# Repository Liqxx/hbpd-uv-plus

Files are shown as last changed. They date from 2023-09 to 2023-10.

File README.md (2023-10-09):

# HBPD-UV+ light pulsers

This repository describes the sub-ns and high-power UV/Vis pulsed diode design package **HBPD-UV+** developed by Felix Henningsen and Nicolas Braam.

## Contact
* Felix Henningsen (felix_henningsen@sfu.ca)
* Nicolas Braam (nbraam@uvic.ca)

## Warning
The drivers described in this repository carry the potential to emit intense ultraviolet light and high peak-power laser radiation when used with light emitting diodes or laser diodes. Exposure to these optical pulses can lead to adverse health effects and permanent vision damage.

It is the user's full responsibility to adhere to appropriate laser safety procedures to avoid any eye or skin exposure and related health consequences.

## Folder structure
#### sub-ns/
* [firmware/](sub-ns/firmware) - Microcontroller firmware
* [manufacture/](sub-ns/manufacture) - Manufacturing files for the printed circuit board design
* [schematic/](sub-ns/schematic) - Schematics for the printed circuit board design
* [userguide/](sub-ns/userguide) - User guide

#### high-power/
* [manufacture/](high-power/manufacture) - Manufacturing files for the printed circuit board design
* [schematic/](high-power/schematic) - Schematics for the printed circuit board design

## File viewer
For viewing the manufacturing Gerber RS-274X files, we recommend the open-source gerber file viewer https://github.com/gerbv/gerbv, or your preferred electronics design software.

## Citation
F. Henningsen, N. Braam *et al* 2023 *JINST* **18** P10010

**DOI** [10.1088/1748-0221/18/10/P10010](https://iopscience.iop.org/article/10.1088/1748-0221/18/10/P10010)

## Licence
Licensing differs for the various sub-components, and license information for all individual packages is included in the respective sub-directories.

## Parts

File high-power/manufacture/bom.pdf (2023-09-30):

## High-power pulser BOM

Part | Populate | Manufacturer | Manufacturer Part # | Supplier | Supplier Part # | Supplier Description | Quantity per Unit
C1,C2,C3,C4 | Yes | Murata Electronics | GRM21BD72A225KE01L | Digikey | 490-GRM21BD72A225KE01LDKR-ND | 2.2 µF ±10% 100V Ceramic Capacitor X7T 0805 (2012 Metric) | 4
C5, C6, C7, C8 | Yes | Murata Electronics | GRM188Z71E225KE43D | Digikey | 490-GRM188Z71E225KE43DTR-ND | 2.2 µF ±10% 25V Ceramic Capacitor X7R 0603 (1608 Metric) | 4
C9,C10,C11,C12,C13 Yes | Samsung Electro-Mechanics | CL10B105KA8NFNC | Digikey | 1276-1942-6-ND | 1 µF ±10% 25V Ceramic Capacitor X7R 0603 (1608 Metric) | 5
C14,C15 | Yes | Vishay Vitramon | VJ0603A120FXXPW1BC | Digikey | 720-VJ0603A120FXXPW1BCDKR-ND | 12 pF ±1% 25V Ceramic Capacitor C0G, NP0 0603 (1608 Metric) | 2
C16,C17 | Yes | Murata Electronics | GCM1555C1H5R0FA16D | Digikey | 490-GCM1555C1H5R0FA16DDKR-ND 5 pF ±1% 50V Ceramic Capacitor C0G, NP0 0402 (1005 Metric) | 2
C18,C19,C20,C21 | Yes | Samsung Electro-Mechanics | CL10B104KC8NNNC | Digikey | 1276-6807-6-ND | 0.1 µF ±10% 100V Ceramic Capacitor X7R 0603 (1608 Metric) | 4
C22 | Yes | Taiyo Yuden | HMK105B7103KVHFE | Digikey | 587-HMK105B7103KVHFECT-ND | 10000 pF ±10% 100V Ceramic Capacitor X7R 0402 (1005 Metric) | 1
C23,C24,C25 | Yes | YAGEO | CC0402KPX7R8BB104 | Digikey | 13-CC0402KPX7R8BB104DKR-ND | 0.1 µF ±10% 25V Ceramic Capacitor X7R 0402 (1005 Metric) | 3
C26 | Yes | TDK Corporation | C0510X5R1C104M030BC | Digikey | 445-13583-6-ND | 0.1 µF ±20% 16V Ceramic Capacitor X5R 0204 (0510 Metric) | 1
D1 | Yes | Rohm | RF05VAM2STR | Digikey | RF05VAM2STR-ND | Diode 200 V 500mA Surface Mount TUMD2S | 1
FB1,FB2,FB3 | Yes | TDK | MPZ1005S331ET000 | Digikey | 445-9330-2-ND | 330 Ohms 1 Power Line Ferrite Bead 0402 (1005 Metric) 700mA 280mOhm | 3
J1,J2 | Yes | TE Connectivity | 1776113-2 | Digikey | A97976-ND | 2 Position Wire to Board Terminal Block Horizontal with Board 0.150" (3.81mm) Through Hole | 2
J3,J5 | Yes | Samtec | MMCX-J-P-H-ST-SM1 | Digikey | SAM8838-ND | MMCX Connector Jack, Female Socket 50Ohm Surface Mount Solder | 2
L1 | Yes | Murata Electronics | LQW18AS3N6G0ZD | Digikey | 490-15826-6-ND | 3.6 nH Unshielded Wirewound Inductor 700 mA 63mOhm Max 0603 (1608 Metric) | 1
Q1 | Yes | EPC | EPC2214 | Digikey | 917-1213-2-ND | N-Channel 80 V 10A (Ta) Surface Mount Die | 1
R1 | Yes | Vishay Dale | RCA080549R9FKEA | Digikey | 541-2220-2-ND | 49.9 Ohms ±1% 0.125W, 1/8W Chip Resistor 0805 (2012 Metric) Anti-Sulfur, Automotive AEC-Q200 Thick Film | 1
R2,R4 | Yes | YAGEO | AC0603FR-07100RL | Digikey | YAG3561DKR-ND | 100 Ohms ±1% 0.1W, 1/10W Chip Resistor 0603 (1608 Metric) Automotive AEC-Q200, Moisture Resistant Thick Film | 2
R3 | Yes | YAGEO | RC0603FR-1356RL | Digikey | 13-RC0603FR-1356RLDKR-ND | 56 Ohms ±1% 0.1W, 1/10W Chip Resistor 0603 (1608 Metric) Thick Film | 1
R5,R6,R7,R8 | Yes | Vishay Dale | CRCW04023R90FKED | Digikey | 541-3.90LLTR-ND | 3.9 Ohms ±1% 0.063W, 1/16W Chip Resistor 0402 (1005 Metric) Automotive AEC-Q200 Thick Film | 4
R9 | Yes | Keystone Electronics | 5108 | Digikey | 36-5108TR-ND | 0 Ohms Jumper Chip Resistor 1206 (3216 Metric) Metal Element | 1
R10 | Yes | Vishay Dale | CRCW0603100KFKEAHP | Digikey | 541-100KSTR-ND | 100 kOhms ±1% 0.333W, 1/3W Chip Resistor 0603 (1608 Metric) Automotive AEC-Q200, Pulse Withstanding Thick Film | 1
R11,R12 | Yes | Stackpole Electronics Inc | RMCF0201ZT0R00 | Digikey | RMCF0201ZT0R00DKR-ND | 0 Ohms Jumper Chip Resistor 0201 (0603 Metric) Thick Film | 2
R13,R14 | Yes | Vishay Dale | CRCW040210R0FKEE | Digikey | 541-CRCW040210R0FKEETR-ND | 10 Ohms ±1% 0.063W, 1/16W Chip Resistor 0402 (1005 Metric) Automotive AEC-Q200 Thick Film | 2
R15 | No | - | - | - | - | | -
R16 | Yes | YAGEO | RC0603FR-072R4L | Digikey | 13-RC0603FR-072R4LTR-ND | 2.4 Ohms ±1% 0.1W, 1/10W Chip Resistor 0603 (1608 Metric) Moisture Resistant Thick Film | 1
R17 | Yes | Panasonic | ERA-2AEB102X | Digikey | P1.0KDCTR-ND | 1 kOhms ±0.1% 0.063W, 1/16W Chip Resistor 0402 (1005 Metric) Automotive AEC-Q200 Thin Film | 1
R18 | Yes | Panasonic | ERA-2AEB49R9X | Digikey | P49.9DCTR-ND | 49.9 Ohms ±0.1% 0.063W, 1/16W Chip Resistor 0402 (1005 Metric) Automotive AEC-Q200 Thin Film | 1
U1 | Yes | Microchip Technology | MCP1703T-5002E/MC | Digikey | MCP1703T-5002E/MCTR-ND | Linear Voltage Regulator IC Positive Fixed 1 Output 250mA 8-DFN (2x3) | 1
U2 | No | Microchip Technology | MCP1703T-3302E/CB | - | - | | -
U3,U4 | Yes | onsemi | NC7WZ16L6X | Digikey | NC7WZ16L6XTR-ND | Buffer, Non-Inverting 2 Element 1 Bit per Element Push-Pull Output 6-MicroPak | 2
U5 | Yes | Texas Instruments | LMG1020YFFR | Digikey | 296-50208-2-ND | Low-Side Gate Driver IC Inverting, Non-Inverting 6-DSBGA | 1
| | | | | | | 58

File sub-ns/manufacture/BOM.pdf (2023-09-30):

## LED Pulser BOM:

Electronic Components

Part Reference | Manufacturer | Manufacturer Part # | Description | Supplier | Supplier Part #

Quantity
for One
Unit
C1,C17,C29,C44,C60,C64,C66,C70,C71,C72,C73,C74,C75,C76 | Murata Electronics | GCM155R71H104KE02J | CAP CER 0.1UF 50V X7R 0402 | Digikey | 490‐14514‐1‐ND | 14
C2,C18,C30,C45,C61,C65,C67,C68,C69 | Samsung Electro‐Mechanics | CL10B105MO8NNWC | CAP CER 1UF 16V X7R 0603 | Digikey | 1276‐6524‐1‐ND | 9
C3,C10,C19,C24,C31,C38,C46 | TDK Corporation | C0510X5R0J105M030BC | CAP CER 1UF 6.3V X5R 0204 | Digikey | 445‐9091‐1‐ND | 7
C4,C11,C20,C25,C32,C39,C47 | Murata Electronics | NFM15PC474R0J3D | CAP FEEDTHRU 0.47UF 6.3V 0402 | Digikey | 490‐16920‐1‐ND | 7
C5,C6,C12,C13,C21,C22,C26,C27,C33,C34,C40,C41,C48,C49,C77,C78,C79,C80,C81,C82,C83 | TDK Corporation | C0510X7R1E473M030BA | CAP CER 0.047UF 25V X7R 0204 | Digikey | 445‐C0510X7R1E473M030BACT‐ND | 21
C7,C9,C14,C16,C35,C37,C42 | Murata Electronics | GCM155R71E103KA37D | CAP CER 10000PF 25V X7R 0402 | Digikey | 490‐6043‐1‐ND | 7
C8,C15,C23,C28,C36,C43,C50 | KYOCERA AVX | 0201ZK4R7BBSTR | CAP THIN FILM 4.7PF 10V 0201 | Digikey | 478‐4386‐1‐ND | 7
C51,C53,C62,C63 | TDK Corporation | C2012X5R1E475K125AB | CAP CER 4.7UF 25V X5R 0805 | Digikey | 445‐4116‐1‐ND | 4
C52,C57,C59 | Murata Electronics | GCM155R71H103KA55D | CAP CER 10000PF 50V X7R 0402 | Digikey | 490‐4762‐1‐ND | 3
C54,C55,C56,C58 | TDK Corporation | CGA4J1X7S1E106K125AC | CAP CER 10UF 25V X7S 0805 | Digikey | 445‐181405‐1‐ND | 4
D1 | Rohm Semiconductor | SML013BNTT86 | CHIP LED WITH REFLECTOR: SML‐01 | Digikey | 846‐SML013BNTT86CT‐ND | 1
D2 | Vishay Semiconductor Opto Division | VLMU3100‐GS08 | EMITTER UV 405NM 30MA PLCC | Digikey | VLMU3100‐GS08CT‐ND | 1
D3 | LC LED | UT‐69UV365P | LED 0603 UV SMD LED 365nm | LC LED | UT‐69UV365P | 1
D4 | Photon Wave | PKE‐02‐F35 | LED 295nm 15mW 3535 | IRTRONIX Inc | PKE‐10‐F35 | 1
D5 | Photon Wave | PKD‐02‐F35 | LED 278nm 3.5mW 3535 | IRTRONIX Inc | PKD‐02‐F35 | 1
D6 | Photon Wave | PKB‐02‐F35 | LED 255nm 3.5mW 3535 | IRTRONIX Inc | PKB‐02‐F35 | 1
D7 | Silanna UV | SF1‐3C3FWL1 | LED 235nm 0.45mW 3535 | Silanna UV | SF1‐3C3FWL1‐TR | 1
D8 | SMC Diode Solutions | DSS14U | SCHOTTKY 40V SOD‐123FL | Digikey | 1655‐DSS14UCT‐ND | 1
D9 | Diodes Incorporated | SMAJ5.0A‐13‐F | TVS DIODE 5VWM 9.2VC SMA | Digikey | SMAJ5.0A‐FDICT‐ND | 1
D10,D11,D12,D13 | Semtech Corporation | RCLAMP3331ZATFT | TVS DIODE 3.3V 7.5V SLP0603P2X3F | Digikey | RCLAMP3331ZATFTCT‐ND | 4
J1,J2,J3,J4,J5,J6,J7 | Molex | 734152063 | CONN MMCX JACK STR 50 OHM SMD | Digikey | WM3914CT‐ND | 7
J8 | CUI Inc. | PJ‐037AH | CONN PWR JACK 2X5.5MM SOLDER | Digikey | CP‐037AH‐ND | 1
J9,J10 | Molex | 734152063 | CONN MMCX JACK STR 50 OHM SMD | Digikey | WM3914CT‐ND | 2
J11 | METZ CONNECT USA Inc. | PR20204VBNN | PIN HEADER, THR, SINGLE ROW, .10 | Digikey | 1849‐PR20204VBNN‐ND | 1
J12 | Amphenol ICC (FCI) | 78208‐106HLF | CONN HEADER R/A 6POS 2.54MM | Digikey | 609‐2452‐ND | 1
L1,L2,L3,L4,L5,L6,L7 | Delta Electronics/Components | 0402HC‐3N6EDTS | FIXED IND 3.6NH 900MA 40MOHM SMD | Digikey | 2035‐1343‐1‐ND | 7
L8 | Sumida America Components Inc. | CDRH4D16FB/NP‐100MC | FIXED IND 10UH 1.2A 118 MOHM SMD | Digikey | 308‐2011‐1‐ND | 1
Q1,Q2,Q3,Q4,Q5,Q6,Q7 | EPC | EPC8004 | GANFET N‐CH 40V 4A DIE | Digikey | 917‐1072‐1‐ND | 7
R3,R9,R23,R27,R35,R41,R53,R67,R73 | Yageo | RC0402FR‐07100RL | RES SMD 100 OHM 1% 1/16W 0402 | Digikey | 311‐100LRCT‐ND | 9
R4,R6,R14,R16,R24,R25,R30,R31,R36,R37,R46,R48,R54,R55 | Vishay Dale | CRCW02012R00FXED | RES SMD 2 OHM 1% 1/20W 0201 | Digikey | 541‐CRCW02012R00FXEDCT‐ND | 14
R5,R10,R15,R19,R38,R42,R47,R72,R74 | YAGEO | RC0402FR‐071KL | RES 1K OHM 1% 1/16W 0402 | Digikey | 311‐1.00KLRCT‐ND | 9
R7,R18,R26,R32,R39,R50,R56 | Vishay Dale | CRCW020168R0FKED | RES SMD 68 OHM 1% 1/20W 0201 | Digikey | 541‐68.0AABCT‐ND | 7
R8,R12,R17,R20,R40,R44,R49 | YAGEO | RC0402FR‐0749R9L | RES 49.9 OHM 1% 1/16W 0402 | Digikey | 311‐49.9LRCT‐ND | 7
R2,R13,R29,R34,R45,R52 | YAGEO | RC0402JR‐074R3L | RES 4.3 OHM 5% 1/16W 0402 | Digikey | 311‐4.3JRCT‐ND | 6
R22 | YAGEO | RC0402JR‐072R2L | RES 2.2 OHM 5% 1/16W 0402 | Digikey | 311‐2.2JRCT‐ND | 1
R58 | Bel Fuse Inc. | 0ZCF0030FF2C | PTC RESET FUSE 60V 300MA 2920 | Digikey | 507‐1740‐1‐ND | 1
R59 | Samsung Electro‐Mechanics | RC1005F205CS | RES SMD 2M OHM 1% 1/16W 0402 | Digikey | 1276‐4293‐1‐ND | 1
R60,R65,R66,R69,R71,R80 | Samsung Electro‐Mechanics | RC1005F103CS | RES SMD 10K OHM 1% 1/16W 0402 | Digikey | 1276‐3431‐1‐ND | 6
R62 | YAGEO | RC0402FR‐07169KL | RES 169K OHM 1% 1/16W 0402 | Digikey | YAG3000CT‐ND | 1
R63 | YAGEO | RC0402FR‐07200KL | RES 200K OHM 1% 1/16W 0402 | Digikey | 311‐200KLRCT‐ND | 1
R64 | YAGEO | RC0402FR‐0753K6L | RES 53.6K OHM 1% 1/16W 0402 | Digikey | 311‐53.6KLRCT‐ND | 1
R68 | Yageo | RC0805FR‐130RL | RES 0 OHM JUMPER 1/8W 0805 | Digikey | 13‐RC0805FR‐130RLCT‐ND | 1
R70 | Yageo | RC0805FR‐0749R9L | RES SMD 49.9 OHM 1% 1/8W 0805 | Digikey | 311‐49.9CRCT‐ND | 1
R76 | YAGEO | RC0402FR‐07330RL | RES 330 OHM 1% 1/16W 0402 | Digikey | 311‐330LRCT‐ND | 1
R77 | YAGEO | RC0402FR‐0740K2L | RES 40.2K OHM 1% 1/16W 0402 | Digikey | 311‐40.2KLRCT‐ND | 1
U1,U4,U8,U11 | Texas Instruments | DS90C402MX/NOPB | IC RECEIVER 0/2 8SOIC | Digikey | 296‐35381‐1‐ND | 4
U2,U3,U5,U6,U7,U9,U10 | Texas Instruments | LMG1020YFFR | IC GATE DRVR LOW‐SIDE 6DSBGA | Digikey | 296‐50208‐1‐ND | 7
U12 | Diodes Incorporated | AP3015AKTR‐G1 | IC REG BOOST ADJ 75MA SOT23‐5 | Digikey | AP3015AKTR‐G1DICT‐ND | 1
U13 | Analog Devices Inc. | ADP122AUJZ‐3.3‐R7 | IC REG LINEAR 3.3V 300MA TSOT5 | Digikey | 505‐ADP122AUJZ‐3.3‐R7CT‐ND | 1
U14 | Analog Devices Inc. | LT3061EMS8E#TRPBF | IC REG LIN POS ADJ 100MA 8MSOP | Digikey | LT3061EMS8E#TRPBFCT‐ND | 1
U15 | Texas Instruments | DS90LV018ATMX/NOPB | IC RECEIVER 0/1 8SOIC | Digikey | DS90LV018ATMX/NOPBCT‐ND | 1
U16 | Analog Devices Inc. | ADP7118AUJZ‐5.0‐R7 | IC REG LINEAR 5V 200MA TSOT23‐5 | Digikey | 505‐ADP7118AUJZ‐5.0‐R7CT‐ND | 1
U18 | Diodes Incorporated | AP22804AW5‐7 | IC PWR SWITCH P‐CHAN 1:1 SOT25 | Digikey | AP22804AW5‐7DICT‐ND | 1
U17 | Texas Instruments | DS90LV011AQMFE/NOPB | IC DRIVER 1/0 SOT23‐5 | Digikey | DS90LV011AQMFE/NOPBCT‐ND | 1
U19 | Microchip Technology | AVR64DD32‐I/RXB | 64KB, 8KB RAM, 32P, 24MHZ, MVIO, | Digikey | 150‐AVR64DD32‐I/RXB‐ND | 1
U20 | Skyworks Solutions, Inc. | SI53315‐B‐GM | Clock Buffer Universal 2:10 low‐jitter clock buffer/leve Mouser | 634‐SI53315‐B‐GM | 1
Y1 | Murata Electronics | CSTNE24M0VH3C000R0 | 3.2X1.3MM 24.0MHZ CERAMIC RESONA | Digikey | 490‐CSTNE24M0VH3C000R0CT‐ND | 1

Power Adapter, Comm Cable, Fibers:
Part Reference Manufacturer Manufacturer Part # Description Supplier Supplier Part # | Quantity for One Unit
J12 FTDI TTL‐232R‐3V3 CABLE USB EMBD UART 3.3V .1"HDR Digikey 768‐1015‐ND D1 Thorlabs M80L005 Ø200 µm Core, 0.22 NA, FC/PC to Ø2.5 mm Ferrule PatThorlabs M80L005 Taoglas Limited CAB.01402 CBL ASSY SMA‐MMCX RG174 3.937" Digikey 931‐1099‐ND D1 Bivar Inc. SMFLP36.0 LIGHT PIPE FLEXIBLE CLEAR 4MM Digikey SMFLP36.0‐ND J8 CUI Inc. SWI6‐5.9‐N‐P7 AC/DC WALL MNT ADAPTER 5.9V 7.1W Digikey 102‐3608‐ND | 1 1 2 1 1

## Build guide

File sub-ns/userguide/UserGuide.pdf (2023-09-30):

# Light Source User Guide

## Hardware Specification

‐ | Seven LEDs: 468nm, 410nm, 367nm, 295nm, 275nm, 255nm, 235nm
‐ | LEDs flash for <1ns (FWHM)
‐ | Seven (optional) LED cathode MMCX test points to observe LED cathode electronic pulse
‐ | External desktop power adapter
‐ | External Trigger input MMCX coax connector
‐ | DAQ Sync output MMCX coax connector
‐ | Computer control via Serial UART port of: • LED Bias Voltage setting (10 bit DAC)
| • LED Bias Voltage read back (12 bit ADC)
| • LED Channel selection
| • LED Trigger source (external, or internal)
| • Internal trigger rate (fast or slow)
| • Power Down (for standby, low power consumption)

## General Description

The Light Source is designed to operate in a standalone fashion, or with integration to external systems. In standalone fashion, it only needs power, and a serial connection to a computer. If integrated to other systems, it can additionally accept an external trigger, and provides a sync output to DAQ electronics.

Seven LEDs of interest are placed in a row with 8.5mm pitch, spanning 51mm.

The primary calibration LED can accept a light guide assembly.

## Typical Kit Contents

‐ | Light Source Board
‐ | 1 x MMCX‐SMA Cable
‐ | USB to Serial FTDI Cable (TTL‐232R‐3V3)
‐ | +6V 1.2A Power Adapter (SWI6‐5.9‐N‐P5R)
‐ | Bivar light guide assembly (SMFLP36.0)
‐ | Thorlabs fiber optic (M80L005) with modified Bivar base

## User Instructions

### WARNING!! THESE LEDS EMIT POTENTIALLY HARMFUL UV LIGHT. ENSURE LED

LIGHT OUTPUT IS CAREFULLY SHIELDED FROM EYES/SKIN.

1. Please observe anti‐static precautions while touching electronics: such as wearing a grounded protective wrist strap, and working on a grounded anti‐static mat.
2. Cover the UV LEDs (367‐235nm) gently with black electrical tape if temporarily operating in an area where eye/skin exposure can occur. Consider using UV protective eyewear.
3. Mount the board using four screw holes, or place on a non‐conductive work surface (antistatic mat is ideal).
4. Plug the supplied USB FTDI cable into a computer. Ensure drivers work and it exists as a Com Port. (Consult www.ftdichip.com website for instructions). Plug FTDI receptacle into Light Source board with contacts facing up. Black wire is pin 1.

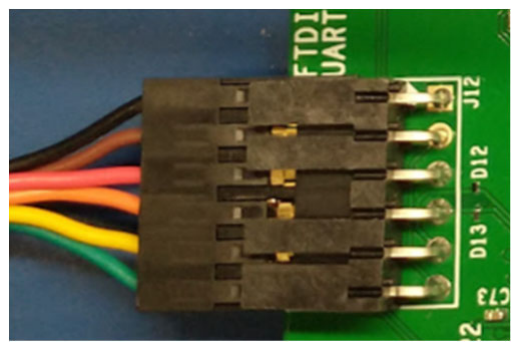
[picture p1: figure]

5. Connect MMCX co‐axial cables if required:
‐ | To observe electronic LED pulse, plug into adjacent MMCX vertical receptacle. Connect
| to oscilloscope input set to 50 Ohms, and maximum bandwidth (>2GHz). Note signal
| amplitude is attenuated by 40x.
‐ | To provide external trigger, plug into ‘Trig In’ receptacle. Use 3.3V logic signal source
| set to drive 50Ohms.
‐ | Plug into ‘Sync Out’ receptacle for DAQ System synchronization. Note this produces
| 3.3V logic signal, but cannot drive 50 Ohms termination (must be high impedance
| termination).
‐ | Always plug/unplug these when the board power is disconnected.

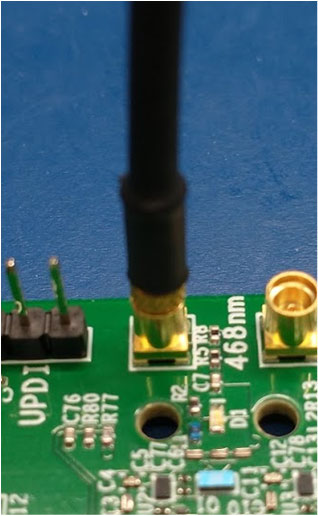
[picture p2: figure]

6. Plug power adapter into a A/C outlet. Plug power adapter barrel connector into Light Source.

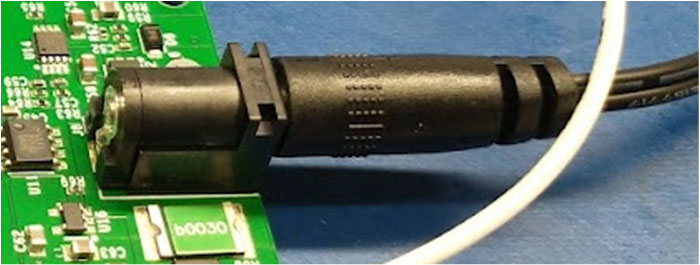
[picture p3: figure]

7. Open a terminal port in Putty or similar program.
‐ | Open a serial connection to the FTDI Com Port
‐ | Use the following settings: • Baud: 115,200
| • Data bits: 8
| • Stop bit: 1
| • Parity: None
| • Flow Control: None
| • Local Echo: On
8. In terminal program, enter any lower case letter to produce ‘Command Menu’. Following is a description of each command:

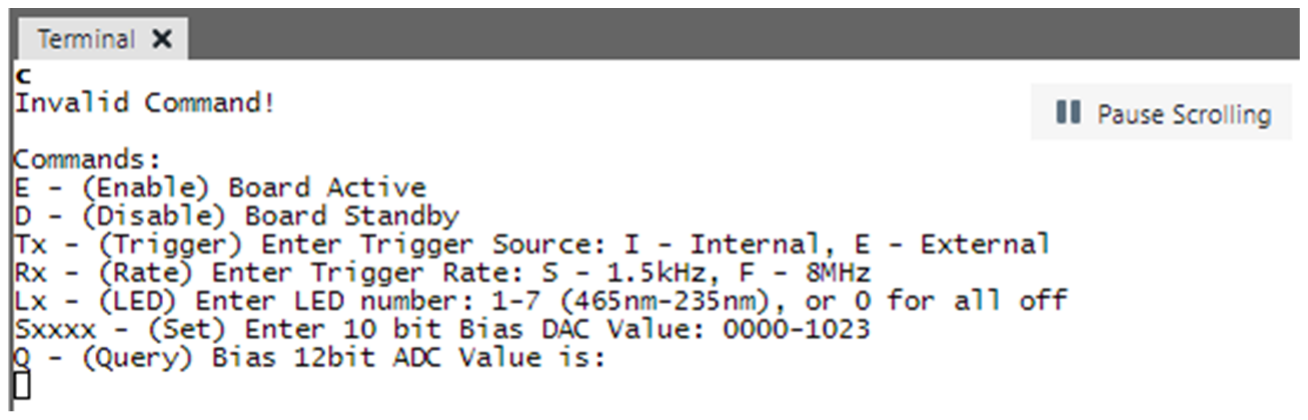
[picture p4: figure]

‐ | E – Enables the Board power, but LEDs are off by default. Current is 350mA maximum.
‐ | D – Disables the Board power (except microcontroller). This drops current to 5mA. Board is disabled by default on power up.
‐ | Tx – Selects Internal or External LED trigger source. Internal is produced by the microcontroller at one of two optional rates. External is introduced by way of the ‘Trig In’ connector. x = I for internal, or E for external.
‐ | Rx – Selects Internal trigger rate. x = S for slow 1.5kHz, or F for fast 8MHz. Use slow trigger rate for all regular data acquisition. Fast rate is used to produce high average light intensity, and can be used for optical alignment procedures.

‐ | Lx – Selects LED, or all off. x = 0,1,2,3,4,5,6,7. 0 turns all LEDs off. 1‐7 selects LEDs 468‐ 235nm respectively. Only one LED will be flashed at a time.

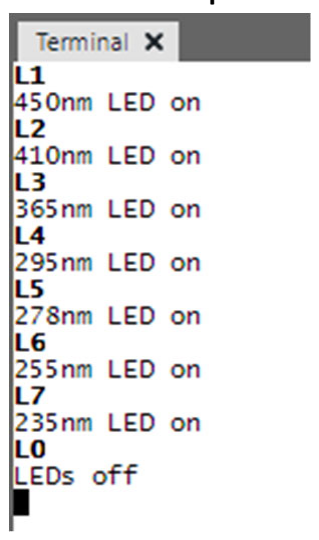
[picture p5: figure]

‐ | Sxxxx – Sets the Bias DAC. The Bias DAC is used to control the LED Bias Voltage. It ranges from ~14.7V to 2.6V. The Bias DAC is 10 bit, so accepts values from 0000‐1023 (2^10). Note the lowest DAC setting is the highest Bias voltage. Bias voltage can be calculated as a function of the DAC setting as follows: Vbias = ((‐ 12.1v/1023)*DAC)+14.7V. Allow 2 seconds for Bias to stabilize.
‐ | Q – Reads the Bias ADC. The Bias ADC is used to read back LED Bias Voltage. The Bias ADC is 12 bit, so produces values from 0‐4095 (2^12). Bias voltage can be calculated from the ADC value as follows: Vbias = ((16.5V/4095)*ADC).
‐ | If some commands are entered when the board is disabled, a message is produced:
‐ | If an invalid character is sent, a message is produced, along with the Command Menu:

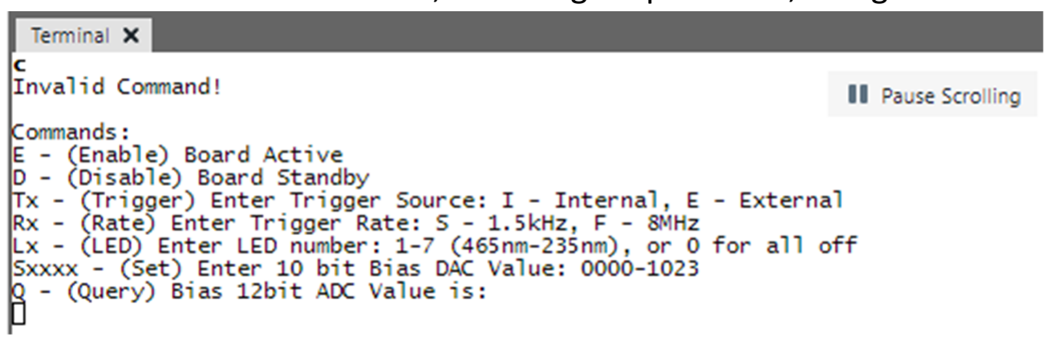
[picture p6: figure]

9. When work is complete always disable the Light Source via the Serial Control before unplugging power.

## General usage notes

### Communication

‐ | If automated control is used to the serial port, some small delays may be required between
| commands/characters: • Allow 500ms after ‘Enable’ for power to stabilize.
| • Allow 100ms between commands, and 10ms between characters.
‐ | Note that incomplete commands will time out after a few seconds.

### LED Intensity

‐ | LED Intensity can be changed on the fly while the LED is actively flashing, but may take 2
| seconds to stabilize.
‐ | Note that LED light intensity is proportional to current. LED current increases exponentially with
| LED bias voltage.
‐ | LED intensity for a given bias voltage will vary depending on the LED model.
‐ | All LEDs are low intensity models. Maximum average intensity will be equivalent to 20mA
| current; typical of a regular indicator LED.

### Bias Voltage

‐ | Bias voltage Set/Read values might be out by 1% from actual voltage due to resistor tolerance.
| This can be improved if it’s a problem.
‐ | Light Source board temperature should be allowed to stabilize before beginning flashing. Allow
| 5 minutes.

### Trigger Rate

‐ | Slow trigger rate is highly recommended when possible: <100kHz. A bias voltage of less than
| 12V should be used at frequencies >100kHz; these LEDs have small dies and a low power rating.
‐ | Although the board will function to 40MHz trigger rate, it is not recommended. Please use
| <10MHz.

### Light Guide and Fiber Coupling

‐ | In PMT testing applications, either the Bivar Light Guide (most efficient) or Thorlabs Fiber Optic
| can be used.
‐ | Press the fiber coupler into the PCB over the LED.
‐ | Mount circuit board in a dark location, or block light with electrical tape or a minimal amount of
| electronics compatible silicone around the Bivar LED adapter (gaps in sides).

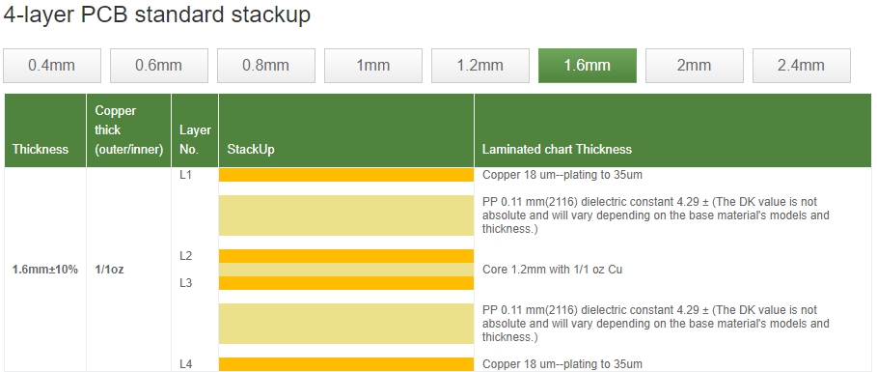
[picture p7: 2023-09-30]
sub-ns/manufacture/Stackup.jpg

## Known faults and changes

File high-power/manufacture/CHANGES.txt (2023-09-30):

Anyone modifying the design should provide brief information about the 
modifications including the date they were made, and that information 
about the design should be added but never removed from this file. 

According to section 3.3.b of the licence, licensees should provide a
brief entry with a date and the nature of the modification for each 
design change. For example: "April 26, 2022: AC/DC power converter 
circuit removed as AC input no longer necessary."

---

DATE		MODIFICATION

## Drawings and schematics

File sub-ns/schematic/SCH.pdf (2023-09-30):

## LVDS Receiver

## FET Gate Driver

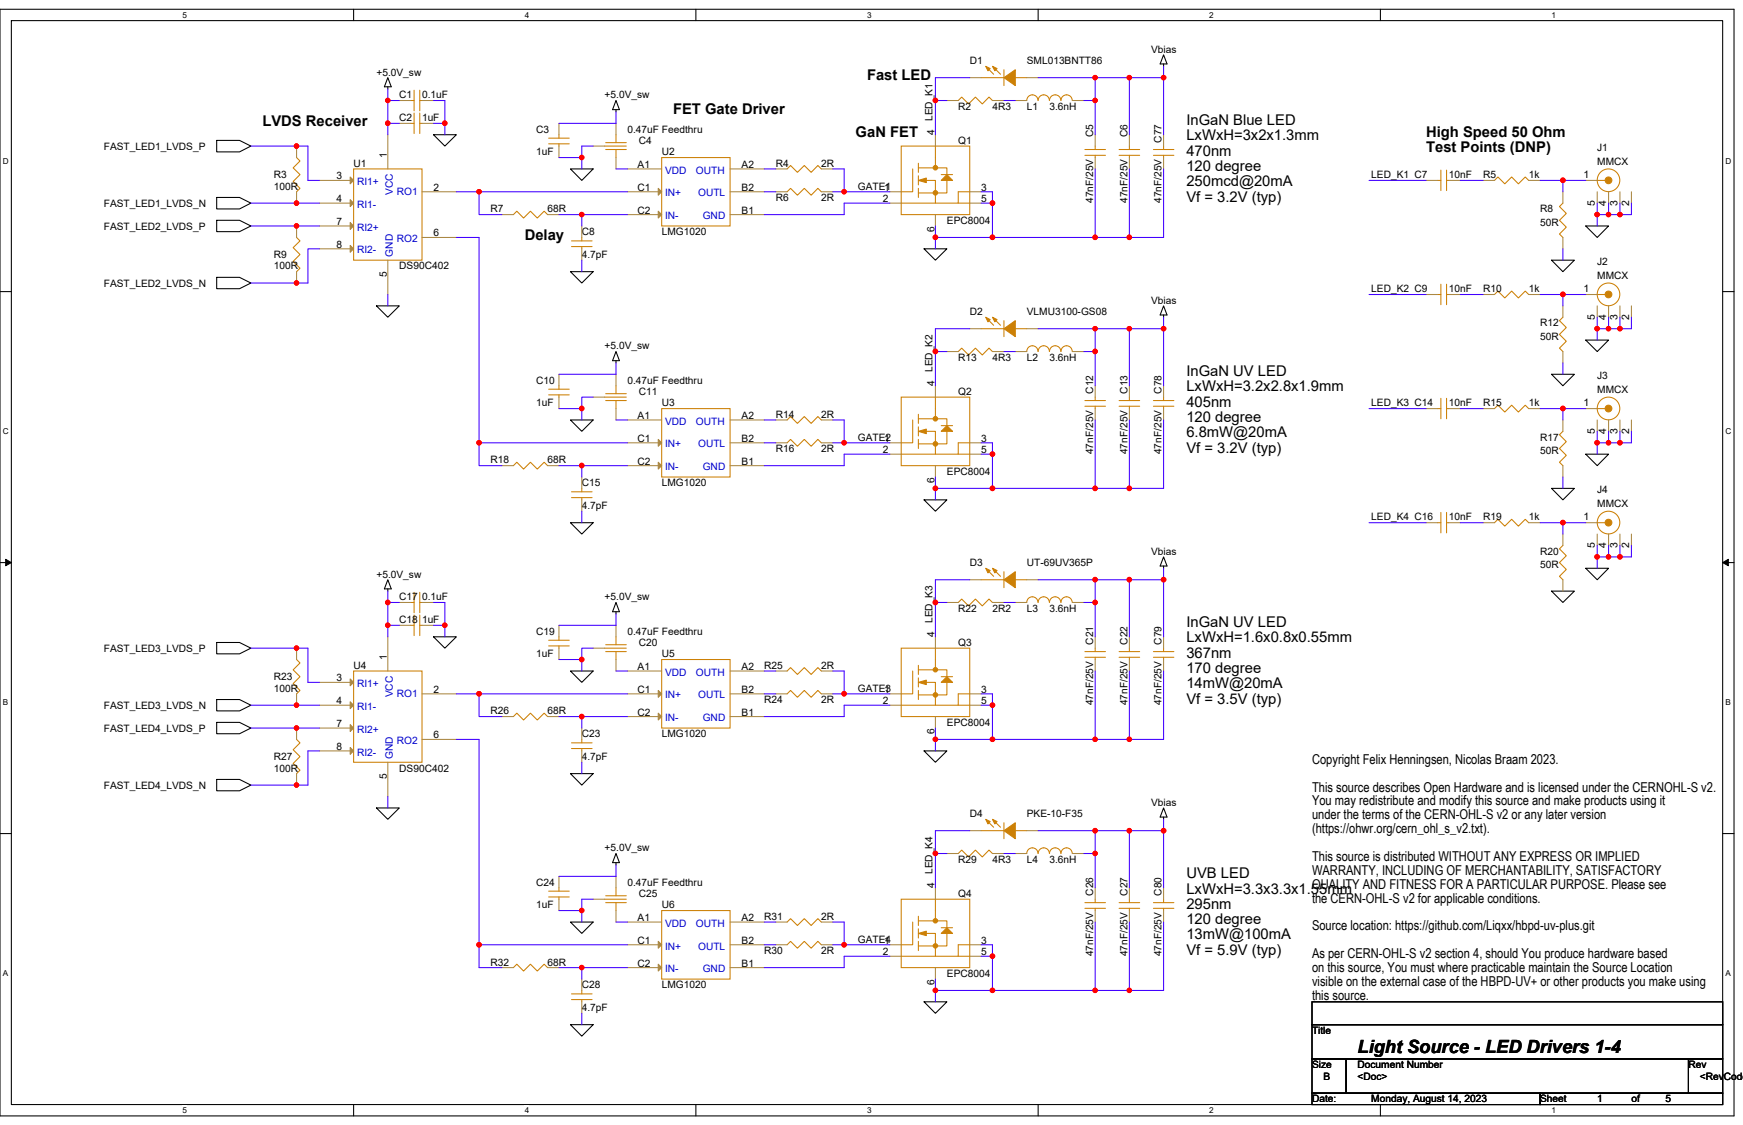
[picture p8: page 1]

Copyright Felix Henningsen, Nicolas Braam 2023.
This source describes Open Hardware and is licensed under the CERNOHL-S v2.
You may redistribute and modify this source and make products using it
under the terms of the CERN-OHL-S v2 or any later version
(https://ohwr.org/cern_ohl_s_v2.txt).
This source is distributed WITHOUT ANY EXPRESS OR IMPLIED
WARRANTY, INCLUDING OF MERCHANTABILITY, SATISFACTORY
QUALITY AND FITNESS FOR A PARTICULAR PURPOSE. Please see
the CERN-OHL-S v2 for applicable conditions.
Source location: https://github.com/Liqxx/hbpd-uv-plus.git
As per CERN-OHL-S v2 section 4, should You produce hardware based
on this source, You must where practicable maintain the Source Location
visible on the external case of the HBPD-UV+ or other products you make using
this source.

Title
Light Source - LED Drivers 1-4

Size Size Size B B B | Document Number Document Number Document Number | Rev Rev Rev

Date: Date: Date: Monday, August 14, 2023 Monday, August 14, 2023 Monday, August 14, 2023 | Sheet Sheet Sheet 1 1 1 of of of 5 5 5

## UVC LED LxWxH=3.5x3.5x1.55mm

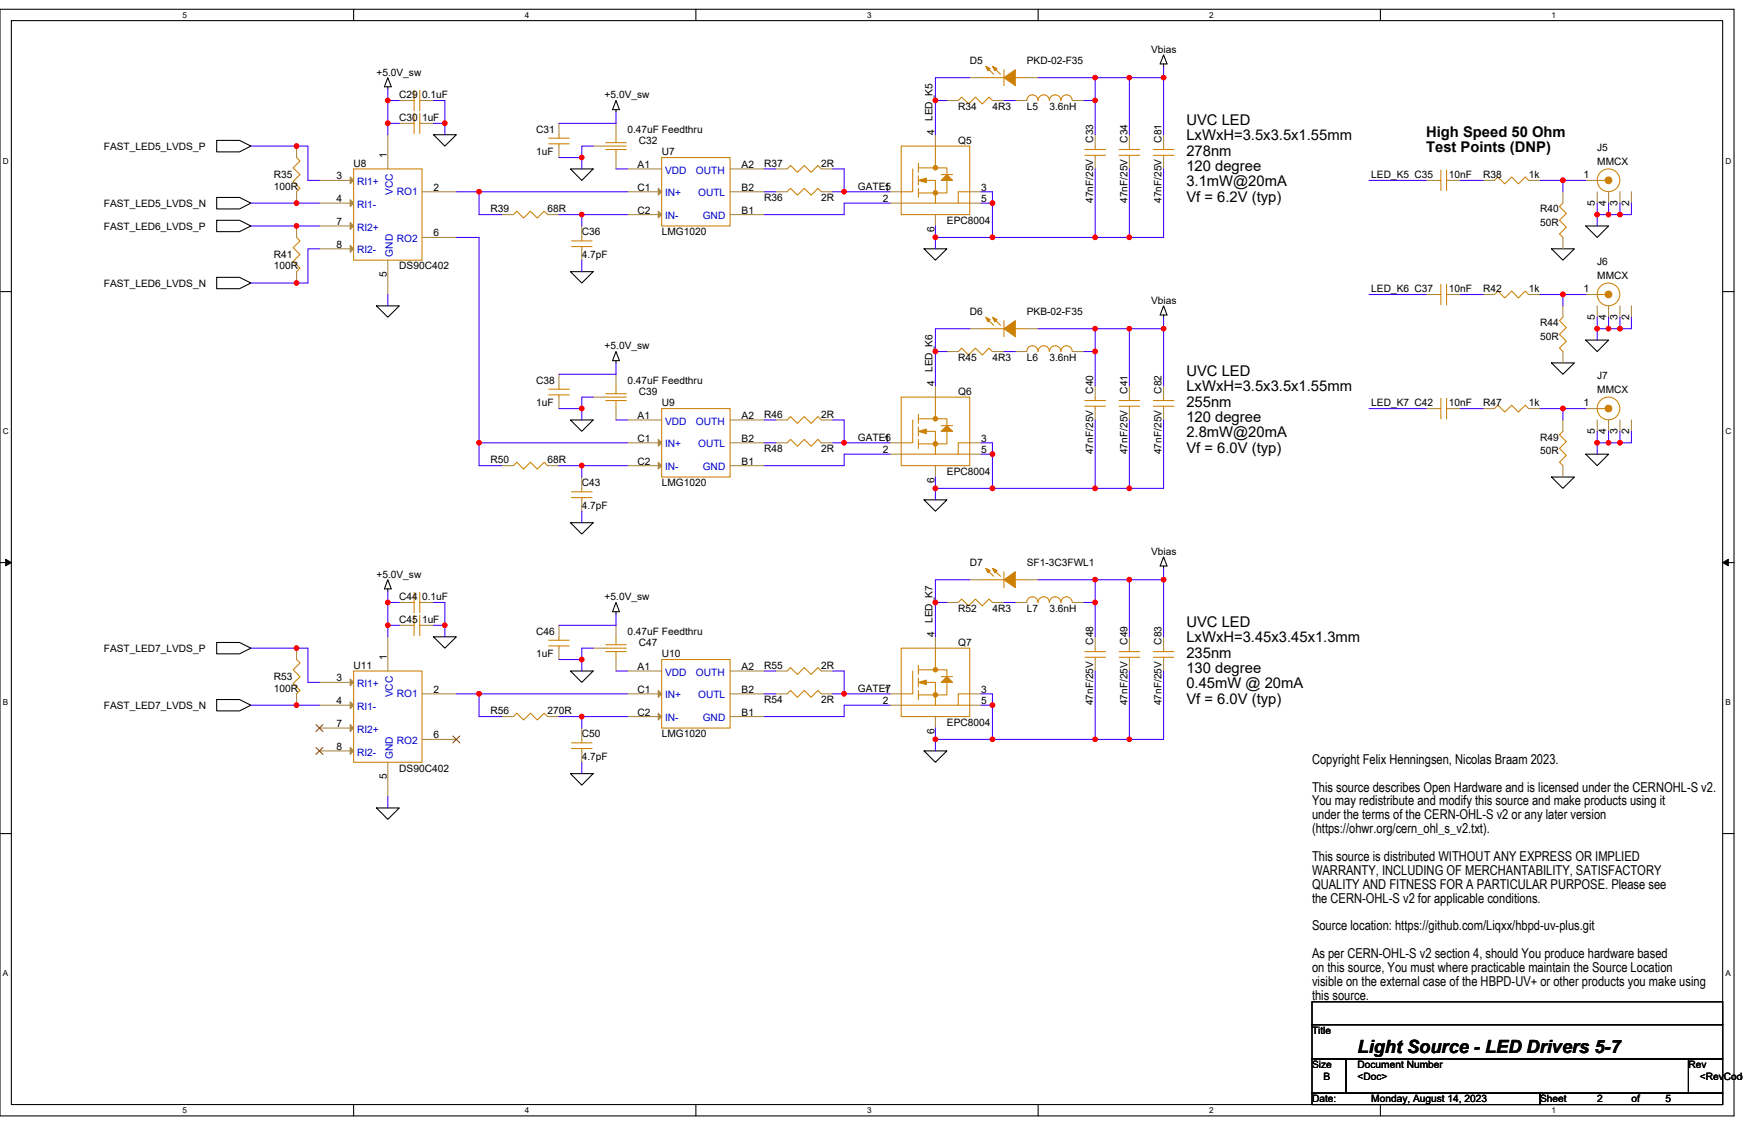
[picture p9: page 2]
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

Title
Light Source - LED Drivers 5-7

Size Size Size B B B | Document Number Document Number Document Number | Rev Rev Rev

Date: Date: Date: Monday, August 14, 2023 Monday, August 14, 2023 Monday, August 14, 2023 | Sheet Sheet Sheet 2 2 2 of of of 5 5 5

## Boost Regulator 16V 100mA

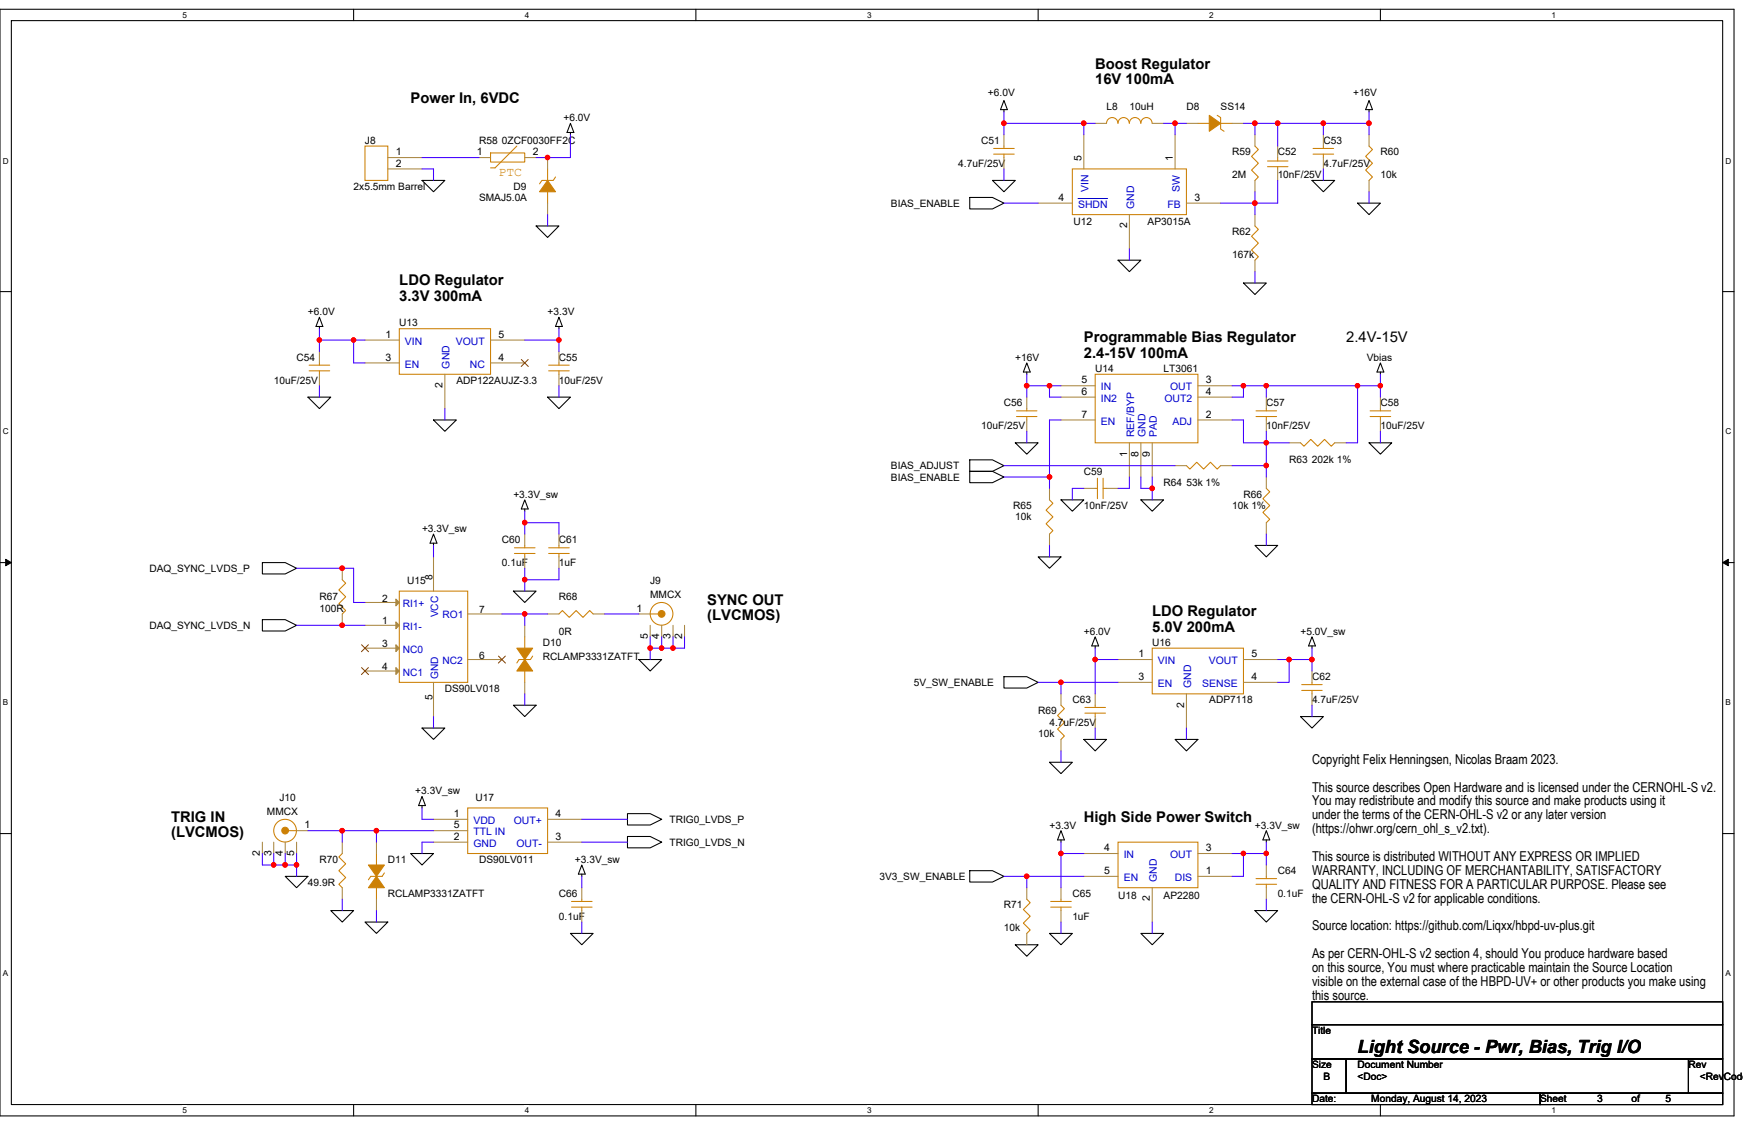
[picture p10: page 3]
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

High Side Power Switch

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

Title
Light Source - Pwr, Bias, Trig I/O

Size Size Size B B B | Document Number Document Number Document Number | Rev Rev Rev

Date: Date: Date: Monday, August 14, 2023 Monday, August 14, 2023 Monday, August 14, 2023 | Sheet Sheet Sheet 3 3 3 of of of 5 5 5

UPDI Programming | Trigger Distribution

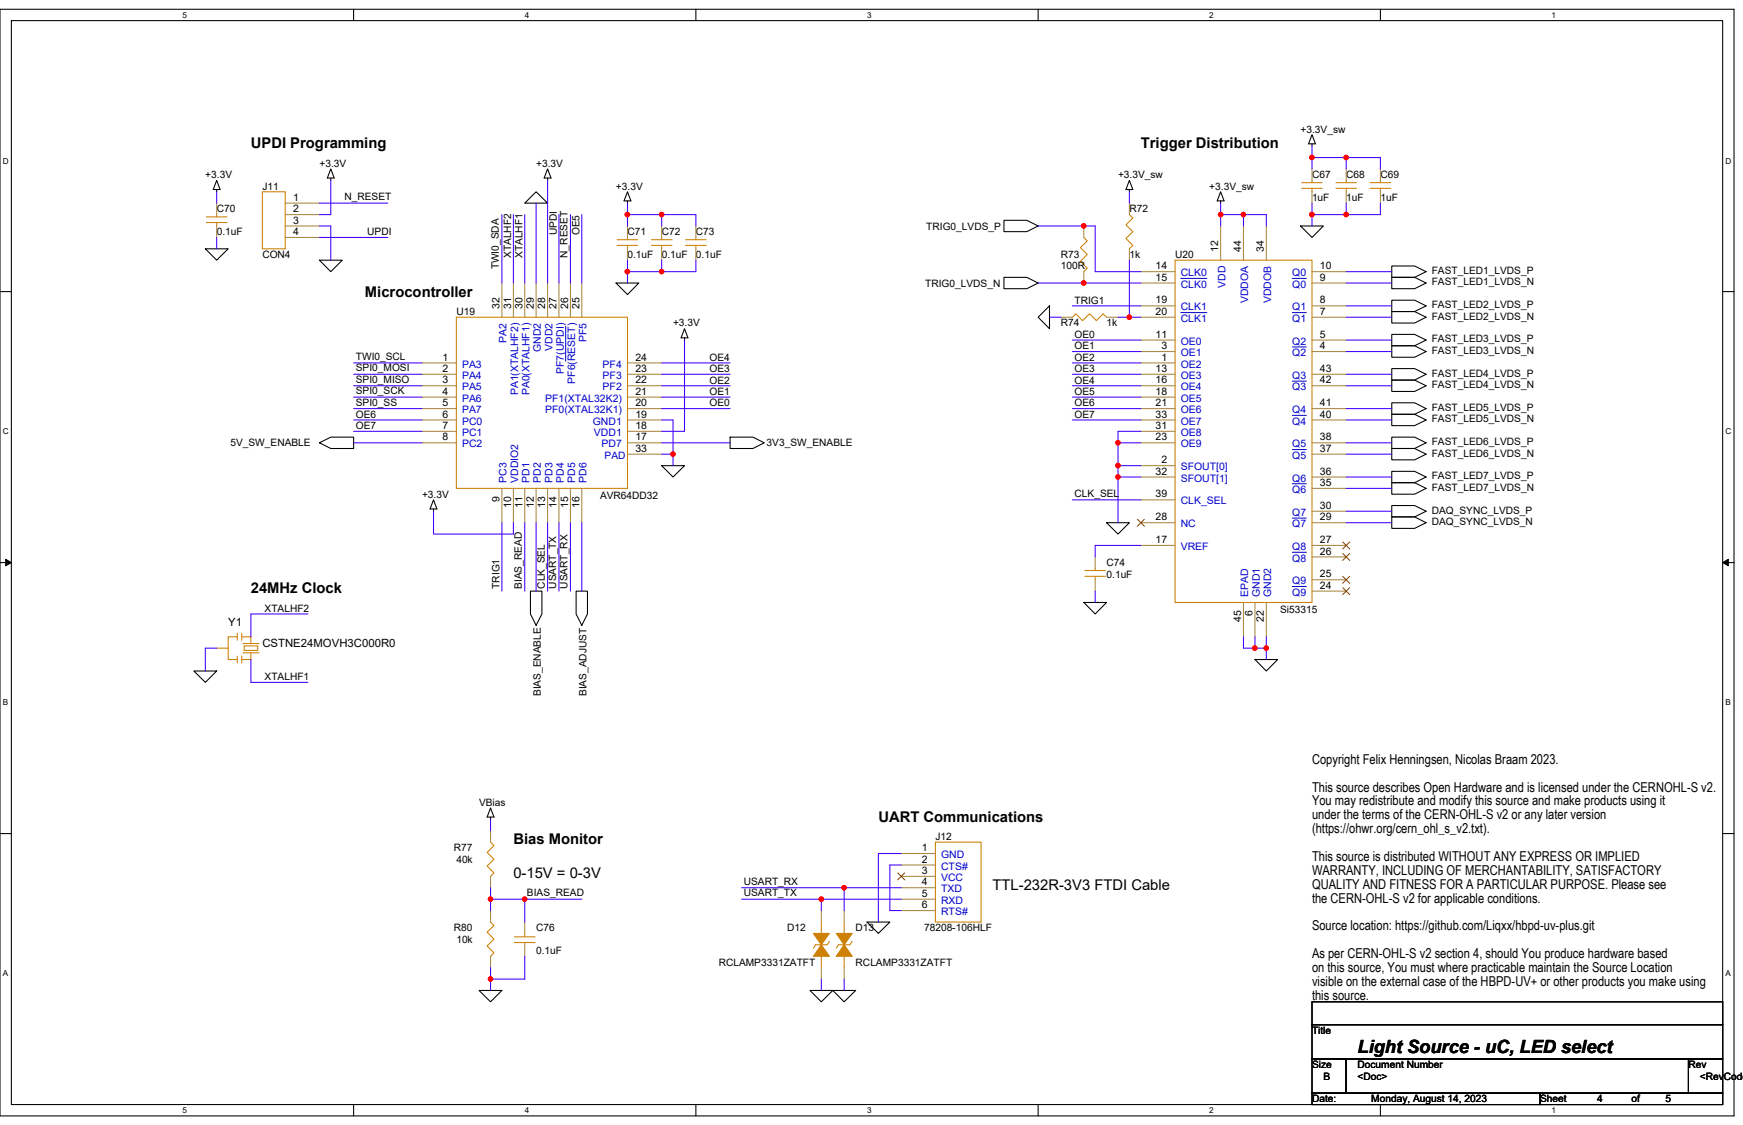
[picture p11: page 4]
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

Title
Light Source - uC, LED select

Size Size Size B B B | Document Number Document Number Document Number | Rev Rev Rev

Date: Date: Date: Monday, August 14, 2023 Monday, August 14, 2023 Monday, August 14, 2023 | Sheet Sheet Sheet 4 4 4 of of of 5 5 5

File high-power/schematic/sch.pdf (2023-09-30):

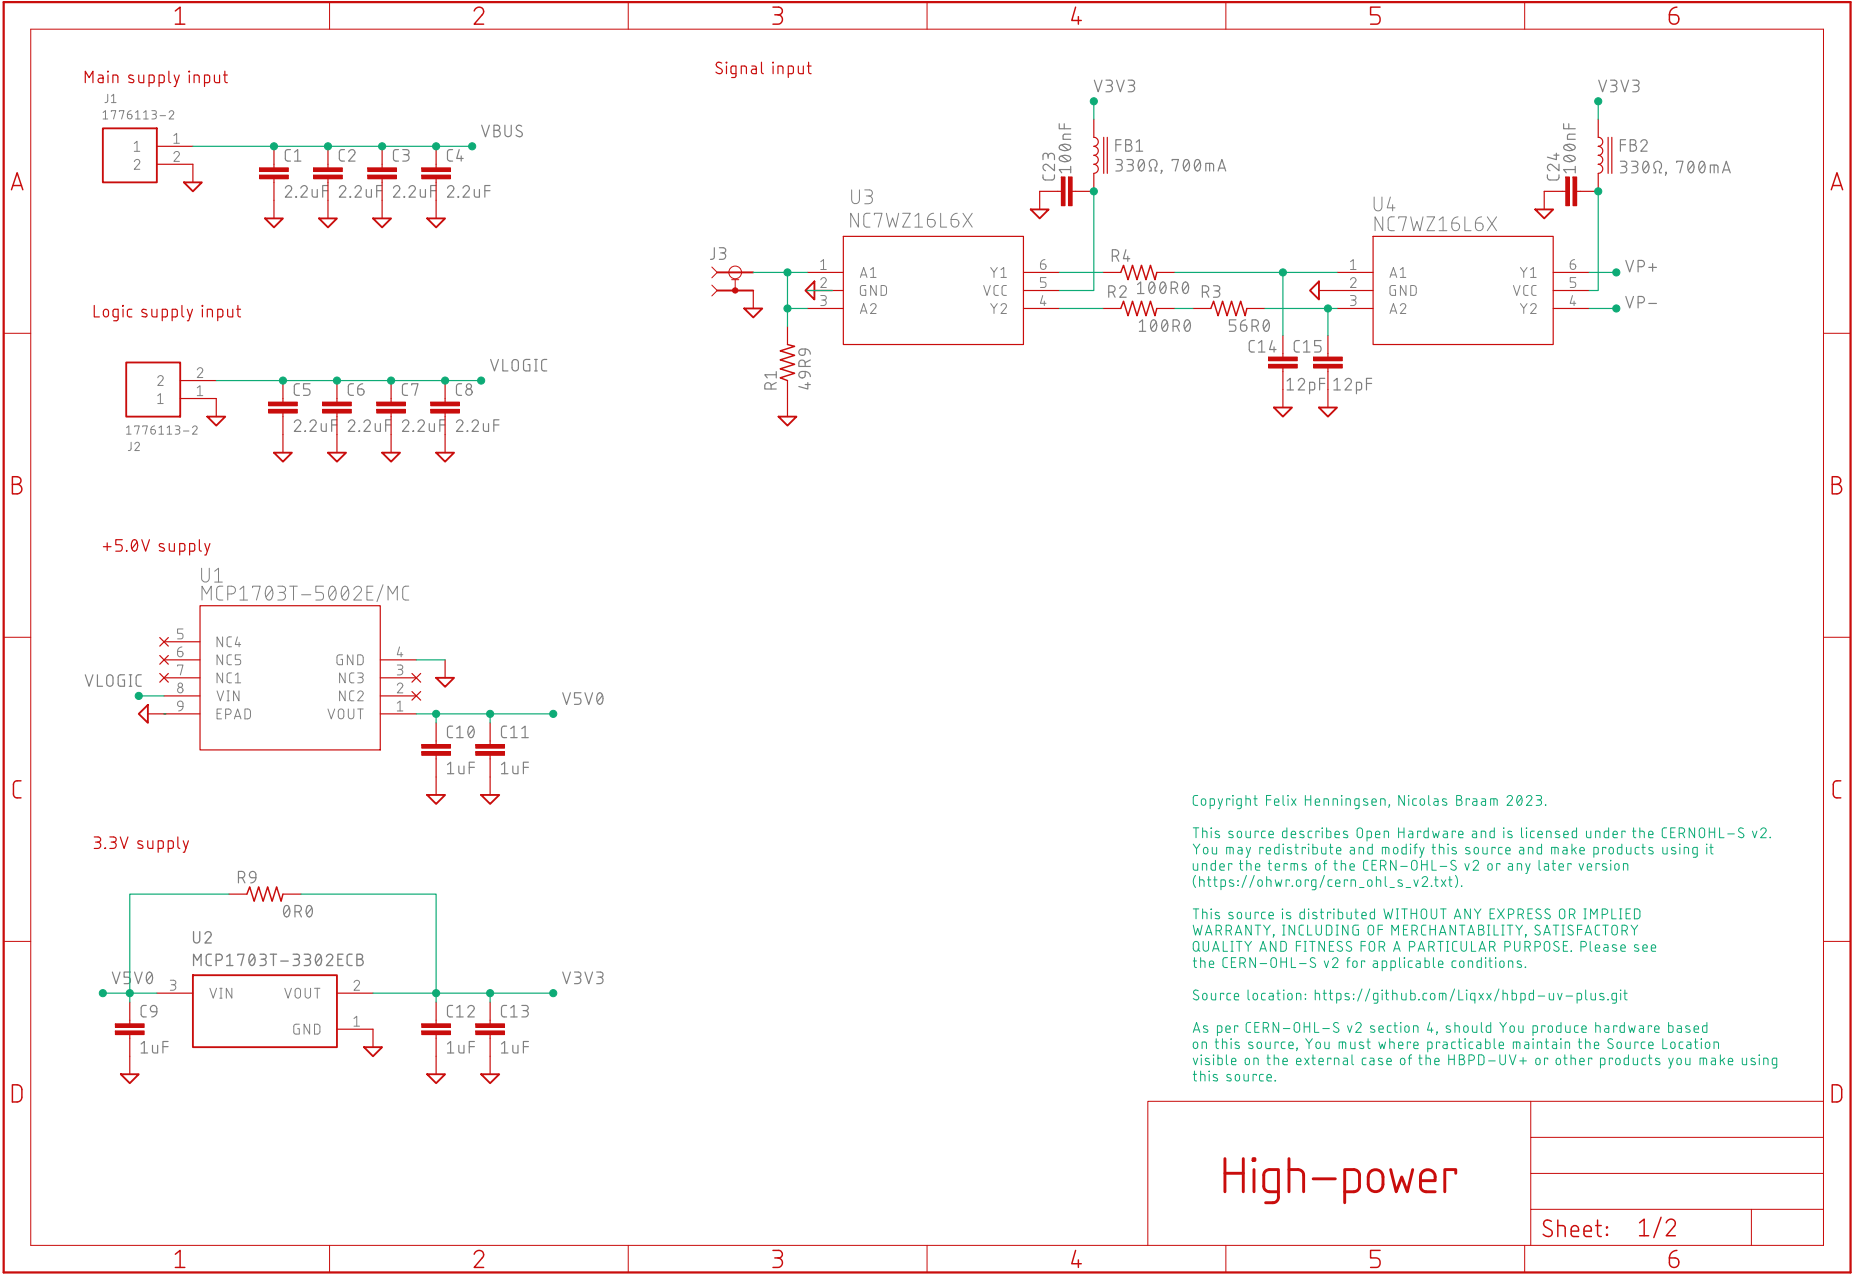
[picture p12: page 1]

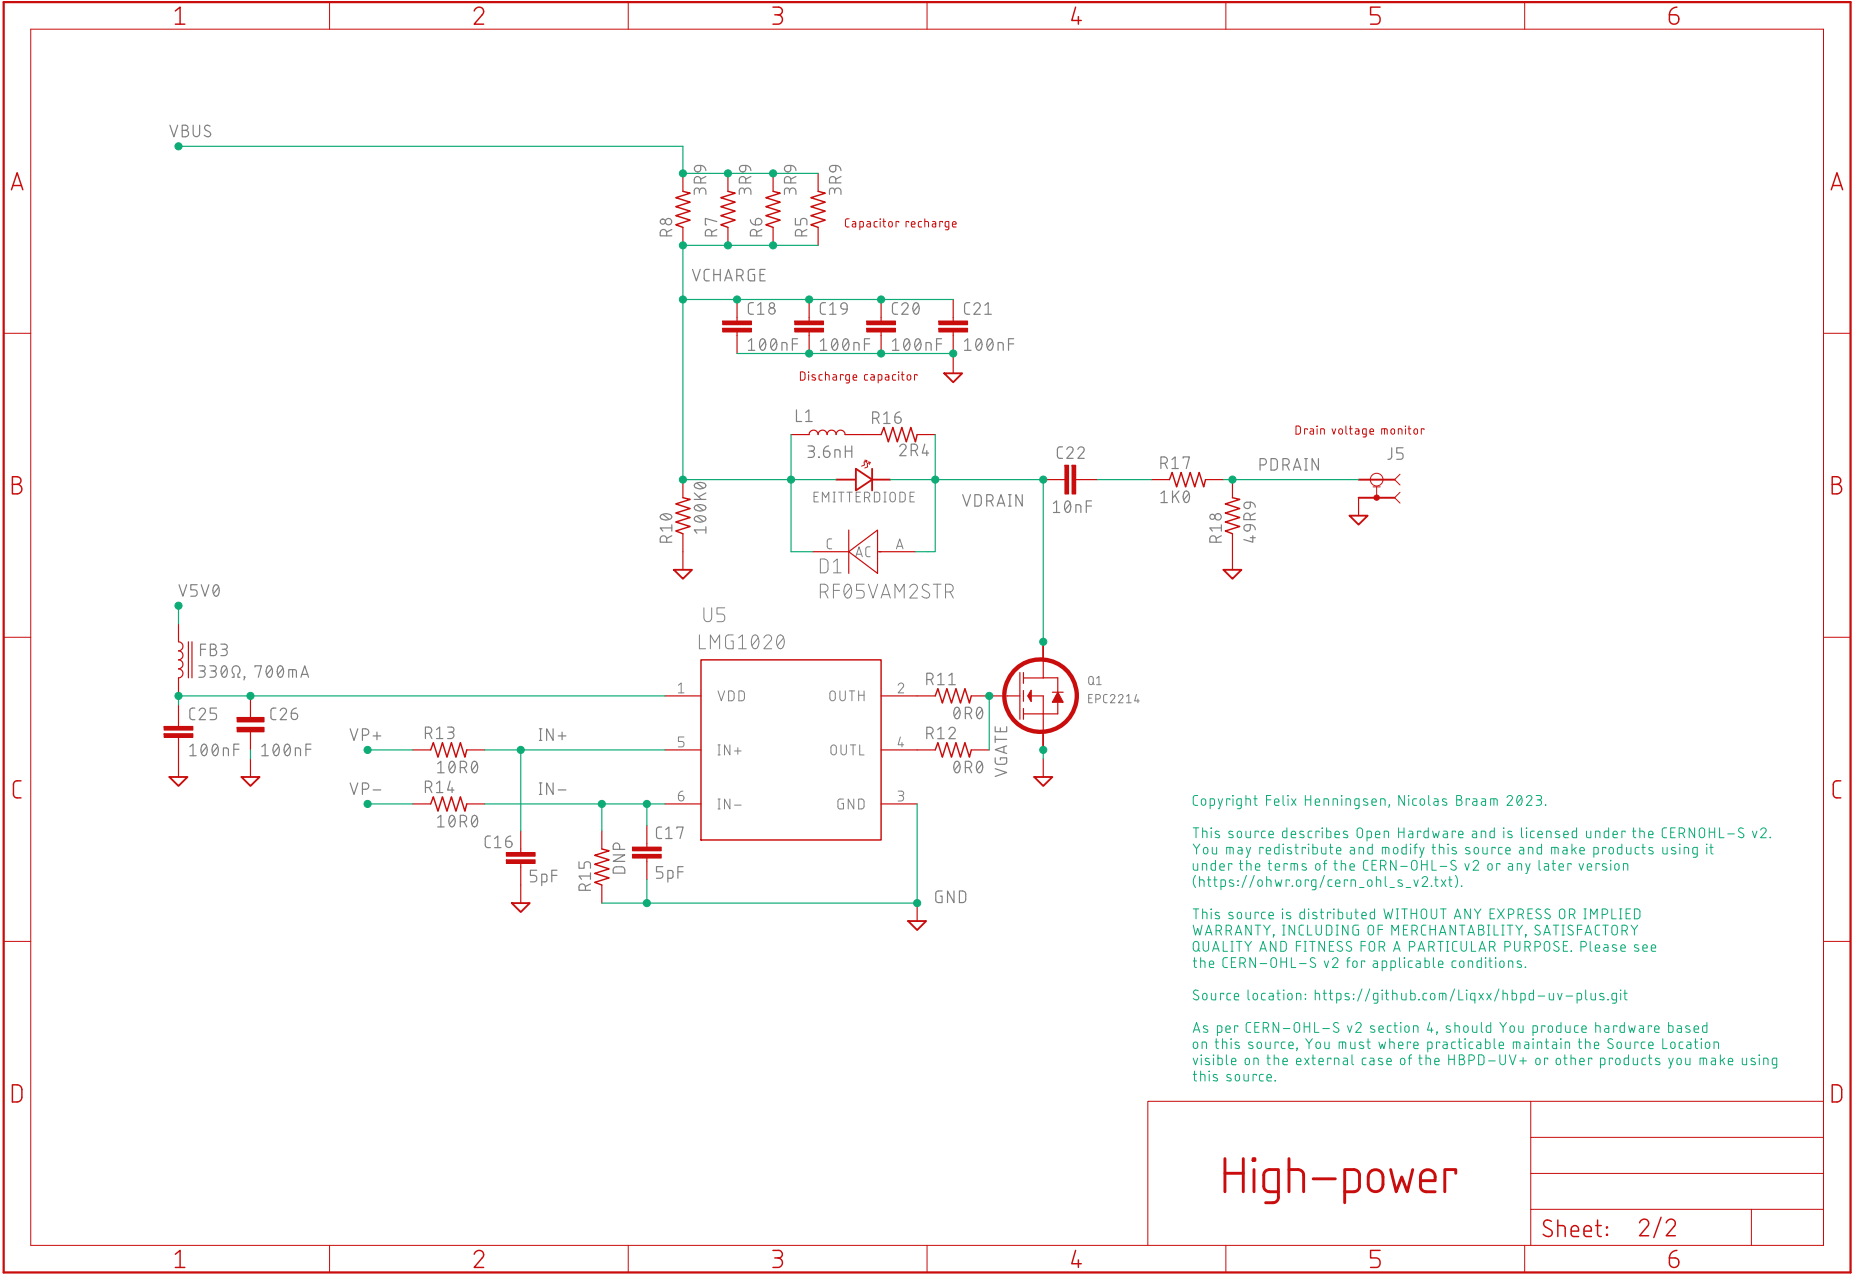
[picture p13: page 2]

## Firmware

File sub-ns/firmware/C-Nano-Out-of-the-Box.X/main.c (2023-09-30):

/*********************************************************************
 *
 *              Water Monitor C Source Code
 *
 *********************************************************************
 * FileName:        main.c
 * Dependencies:    .h
 * Date Started:	Nov 23, 2022
 * Processor:       AVR64DD32   
 * Compiler:        MPLAB XC8 Compiler
 *
 * Notes:
 * 
 * This software is a University of Victoria edited version of Microchip's
 * C-Nano-Out-of-the-Box.X example
 * .  The original source can be found
 * here:
 * 
 * https://github.com/microchip-pic-avr-examples/avr64dd32-cnano-out-of-the-box-code-mplab-mcc/tree/master/C-Nano-Out-of-the-Box.X
 * 
 *   (c) 2018 Microchip Technology Inc. and its subsidiaries. 
 *   
 *   Subject to your compliance with these terms, you may use Microchip software and any 
 *   derivatives exclusively with Microchip products. It is your responsibility to comply with third party 
 *   license terms applicable to your use of third party software (including open source software) that 
 *   may accompany Microchip software.
 *   
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
 *   IN NO EVENT WILL MICROCHIP BE LIABLE FOR ANY INDIRECT, SPECIAL, PUNITIVE, 
 *   INCIDENTAL OR CONSEQUENTIAL LOSS, DAMAGE, COST OR EXPENSE OF ANY KIND 
 *   WHATSOEVER RELATED TO THE SOFTWARE, HOWEVER CAUSED, EVEN IF MICROCHIP 
 *   HAS BEEN ADVISED OF THE POSSIBILITY OR THE DAMAGES ARE FORESEEABLE. TO 
 *   THE FULLEST EXTENT ALLOWED BY LAW, MICROCHIP'S TOTAL LIABILITY ON ALL 
 *   CLAIMS IN ANY WAY RELATED TO THIS SOFTWARE WILL NOT EXCEED THE AMOUNT 
 *   OF FEES, IF ANY, THAT YOU HAVE PAID DIRECTLY TO MICROCHIP FOR THIS 
 *   SOFTWARE.
 *
 * Revision History:
 *
 * Author           Date    		Comment
 *---------------------------------------------------------------------
 * Nicolas Braam	Nov 23, 2022	Started, then got onto other work
 *                  Dec 21, 2022	Frame work good
 *                  Dec 31, 2022    Everything working
 *                  Jan 2, 2023     Refining everything
 *                  Jan 3, 2023     Fix TCA to PC3, more refining, tested all, fixed some small things
 * 
 *
 * Description:
 *
 * This file contains code to be programmed to the Water Monitor
 * Light Source card.  This code assumes 24MHz Fosc.
 *
 ********************************************************************/



/**********************************************************************
 * Libraries:
 **********************************************************************/

#include "mcc_generated_files/mcc.h"
#include <util/delay.h>

/**********************************************************************
 * Constant Definitions:
 **********************************************************************/

#define PWR_DELAY           50                                                  // 50ms
#define RX_DELAY            100                                                 // 100ms
#define VREF_STARTUP_TIME   (50)                                                // VREF start-up time - microseconds
#define LSB_MASK            (0x03)                                              // Mask needed to get the 2 LSb for DAC Data Register
                                                                                /* TMR_CLK = F_CPU / PRESCALER = 4MHz / 4 = 1MHz */
/**********************************************************************
 * Variable Declarations:
 **********************************************************************/

volatile uint16_t adcVal = 0;                                                   // global variable for debug purposes
typedef enum {ACTIVE, STANDBY} programs_t;

static programs_t current_program = STANDBY;

/**********************************************************************
 * Function Prototypes:
 **********************************************************************/

static void WATMON_Initialize(void);                                            // Initialize device
static void CLI_Run(void);
static void CLI_Execute_Command(uint8_t);
static void Print_Menu(void);
static void USART_to_CDC(void);
static uint8_t Unblocking_Read(void);
static uint8_t Read_Parameter(void);                                            // Receive single character
static void Set_Bias_Requested(void);                                           // Receive four characters and write to DAC
static void Send_Bias_Read(void);                                               // Reads ADC and sends value out UART
static void BoardSetStatus(uint8_t);                                            // Enable and disable hardware routines
static void SetTrigger(void);                                                   // Sets trigger source
static void SetRate(void);                                                      // Sets internal trigger source rate
static void SetLED(void);                                                       // Set LED (xor), if any set, then set sync out
static void VREF_init(void);
static void DAC0_init(void);
static void DAC0_setVal(uint16_t val);
static void ADC0_init(void);
static uint16_t ADC0_read(void);
static void TCA0_init(char speed);

/**********************************************************************
 * Interrupt Code:
 **********************************************************************/



/**********************************************************************
 * Main Routine:
 **********************************************************************/

int main (void)
{  
    SYSTEM_Initialize();
    WATMON_Initialize();                                                        // Init specifics of Wat Mon
    VREF_init();
    DAC0_init();
    DAC0_setVal(1023);                                                          // Make sure set low to start
    ADC0_init();
    USART_to_CDC();
    Print_Menu();
	
    while(1)
    {
        CLI_Run();                                                              // Check for data, and do something with it
    }
}



/*********************************************************************
 * Function:        static void WATMON_Initialize(void)
 *
 * PreCondition:    None
 *
 * Input:           None
 *
 * Output:          Microcontroller is initialized
 *
 * Side Effects:    All interrupts and circuit operation are ignored
 *
 * Overview:        Ports and Registers in the Microcontroller are
 *					initialized to the required initial states.
 *
 * Note:            None
 ********************************************************************/

static void WATMON_Initialize(void)
{
// Start up in Disabled mode
    
// Trig distribution OE's, all out, and low

PORTC.DIRSET = PIN1_bm;                                                         // OE7 = PC1, set output, set low
PORTC.OUTCLR = PIN1_bm;

PORTC.DIRSET = PIN0_bm;                                                         // OE6 = PC0, set output, set low
PORTC.OUTCLR = PIN0_bm;

PORTF.DIRSET = PIN5_bm;                                                         // OE5 = PF5, set output, set low
PORTF.OUTCLR = PIN5_bm;

PORTF.DIRSET = PIN4_bm;                                                         // OE4 = PF4, set output, set low
PORTF.OUTCLR = PIN4_bm;

PORTF.DIRSET = PIN3_bm;                                                         // OE3 = PF3, set output, set low
PORTF.OUTCLR = PIN3_bm;

PORTF.DIRSET = PIN2_bm;                                                         // OE2 = PF2, set output, set low
PORTF.OUTCLR = PIN2_bm;

PORTF.DIRSET = PIN1_bm;                                                         // OE1 = PF1, set output, set low
PORTF.OUTCLR = PIN1_bm;

PORTF.DIRSET = PIN0_bm;                                                         // OE0 = PF0, set output, set low
PORTF.OUTCLR = PIN0_bm;

// Trig control, all out, and low

PORTD.DIRSET = PIN3_bm;                                                         // CLK_SEL = PD3, set output, set low
PORTD.OUTCLR = PIN3_bm;

PORTC.DIRSET = PIN3_bm;                                                         // TRIG1 = PC3, set output, set low
PORTC.OUTCLR = PIN3_bm;

// Power control, all out, and low

PORTD.DIRSET = PIN2_bm;                                                         // BIAS_ENABLE = PD2, set output, set low
PORTD.OUTCLR = PIN2_bm;

PORTD.DIRSET = PIN7_bm;                                                         // 3V3_SW_ENABLE = PD7, set output, set low
PORTD.OUTCLR = PIN7_bm;

PORTC.DIRSET = PIN2_bm;                                                         // 5V_SW_ENABLE = PC2, set output, set low
PORTC.OUTCLR = PIN2_bm;

}


/*********************************************************************
 * Function:        static void CLI_Run(void)  
 *
 * PreCondition:    None
 *
 * Input:           None
 *
 * Output:          None
 *
 * Side Effects:    Unknown yet
 *
 * Overview:        Looks for data, if it's received, then call command routine
 *
 ********************************************************************/

static void CLI_Run(void)                                                       // Looks for data
{
    uint8_t ch = 0;
    
    ch = Unblocking_Read();
    
    if((ch != '\n') && (ch != '\r') && (ch != '\0'))                            // If data is valid, execute command
    {
        CLI_Execute_Command(ch);
    }
}


/*********************************************************************
 * Function:        static void CLI_Execute_Command(uint8_t command) 
 *
 * PreCondition:    None
 *
 * Input:           Command received from UART
 *
 * Output:          None
 *
 * Side Effects:    Unknown yet
 *
 * Overview:        Configures Board
 *
 ********************************************************************/


static void CLI_Execute_Command(uint8_t command)
{
    switch(command)
    {
        case 'E':
            BoardSetStatus('E');
            break;
        case 'D':
            BoardSetStatus('D');
            break;
        case 'T':
            SetTrigger();
            break;
        case 'R':
            SetRate();
            break;
        case 'L':
            SetLED();
            break;            
        case 'S':
            Set_Bias_Requested();
            break;
        case 'Q':
            Send_Bias_Read();
            break;
        default:
            printf("\n\rInvalid Command!\n\r");
            Print_Menu();
            break;
    }
}


/*********************************************************************
 * Function:        static void Print_Menu(void) 
 *
 * PreCondition:    None
 *
 * Input:           None
 *
 * Output:          None
 *
 * Side Effects:    Unknown yet
 *
 * Overview:        Prints command menu
 *
 ********************************************************************/

static void Print_Menu(void)                                                    // Menu for print
{
    printf("\n\r");
    printf("Commands:\n\r");
    printf("E - (Enable) Board Active\n\r");
    printf("D - (Disable) Board Standby\n\r");
    printf("Tx - (Trigger) Enter Trigger Source: I - Internal, E - External\n\r");
    printf("Rx - (Rate) Enter Trigger Rate: S - 1.5kHz, F - 8MHz\r\n");
    printf("Lx - (LED) Enter LED number: 1-7 (465nm-235nm), or 0 for all off\r\n");
    printf("Sxxxx - (Set) Enter 10 bit Bias DAC Value: 0000-1023\r\n");
    printf("Q - (Query) Bias 12bit ADC Value is: \r\n");
}



/*********************************************************************
 * Function:        static void USART_to_CDC(void))
 *
 * PreCondition:    None
 *
 * Input:           None
 *
 * Output:          None
 *
 * Side Effects:    Unknown yet
 *
 * Overview:        Configures UART?
 *
 ********************************************************************/

static void USART_to_CDC(void)                                                  // Configure UART?
{
    PORTD.DIRSET = PIN4_bm;
    PORTMUX.USARTROUTEA = PORTMUX_USART0_ALT3_gc;
}
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
